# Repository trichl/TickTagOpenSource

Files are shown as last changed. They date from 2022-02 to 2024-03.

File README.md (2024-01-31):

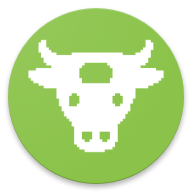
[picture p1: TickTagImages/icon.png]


# I Repository Introduction
This repository contains the entire production-ready design (hardware, software, user interface, 3D-printable housing, assembly instructions) of the open-source TickTag GPS logger.

# II Hardware Production
* See sub folder [TickTagHardware](TickTagHardware)
* Schematics (.sch) and boards (.brd) are designed in Autodesk Eagle 9.5.2
* PCBs were produced and assembled by [PCBWay](https://www.pcbway.com) (production-ready Gerber files and PCBWay settings in [TickTagHardware/GerberProductionFiles](TickTagHardware/GerberProductionFiles))
* Production settings:
   * **REV3**: 24.9 x 10.5 mm, 2 layers, 0.15 mm thickness (flex), 0.35 mm min hole size, immersion gold (ENIG) surface finish (1U"), 0.06 mm min track spacing, 1 oz Cu finished copper, polyimide flex material

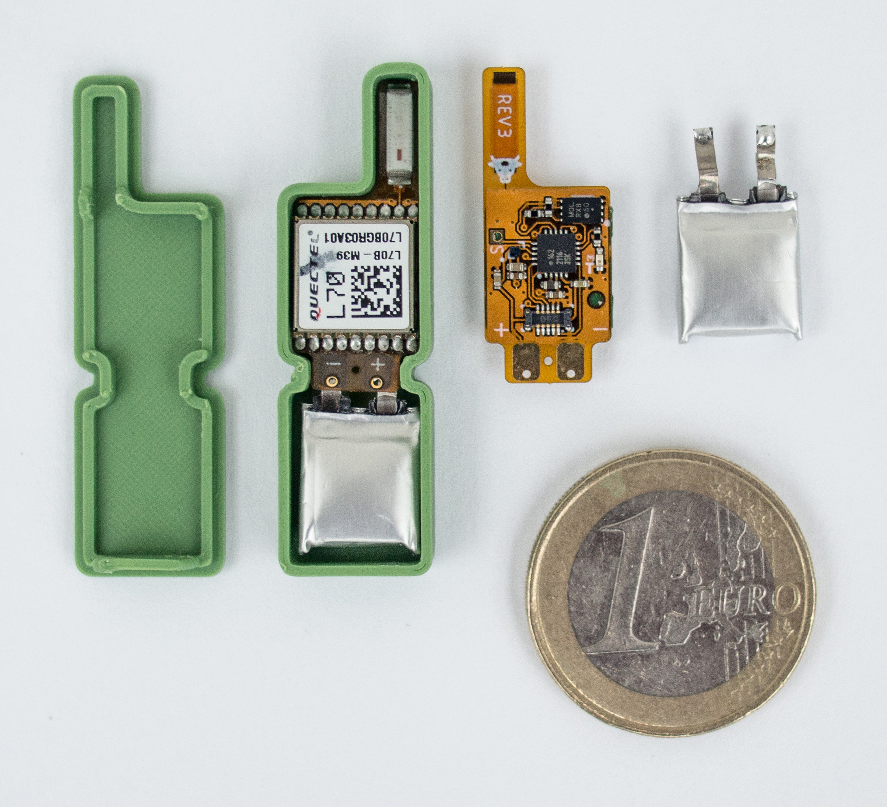
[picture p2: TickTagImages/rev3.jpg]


   * **REV4**: 23.61 x 10.06 mm, 2 layers, 0.2 mm thickness, 0.25 mm min hole size, immersion gold (ENIG) surface finish (1U"), tenting vias, 5/5 mil min track spacing, 1 oz Cu finished copper, FR-4 TG150 material

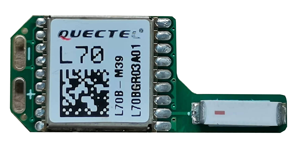
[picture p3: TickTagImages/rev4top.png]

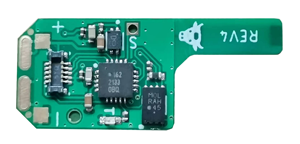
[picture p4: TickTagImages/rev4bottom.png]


   * **User interface board**: 66.4 x 17.8 mm, 2 layers, 1 mm thickness, 0.3 mm min hole size, immersion gold (ENIG) surface finish (1U"), tenting vias, 6/6 mil min track spacing, 1 oz Cu finished copper, FR-4 TG130 material
* Differences between REV3 and REV4:
   * 0.2 mm PCB instead of 0.15 mm (more robust)
   * PCB slots instead of pads for soldering LiPos directly to the PCB
   * New load switch (SiP32431DNP3-T1GE4), as the old load switch has long lead times
   * Reduced the footprint sizes of some of the capacitors and resistors from 0402 to 0201

# III Programming and Assembly

## IDE for Software Development (Windows)
* Atmel Studio 7.0: https://www.microchip.com/en-us/tools-resources/develop/microchip-studio
* Programming language: C / C++

## Android App
* Developed in Android Studio 3.5.1: https://developer.android.com/studio

## Using an Arduino Nano for Flashing
* Follow the instructions on https://github.com/ElTangas/jtag2updi
* The 4.7k resistor is already integrated on the user interface board and does not need to be added
* Alternatively software can be flashed with the official Atmel-ICE: https://www.microchip.com/en-us/development-tool/ATATMEL-ICE

## Flashing the Firmware
Flashing should be done before soldering a battery to the tag.

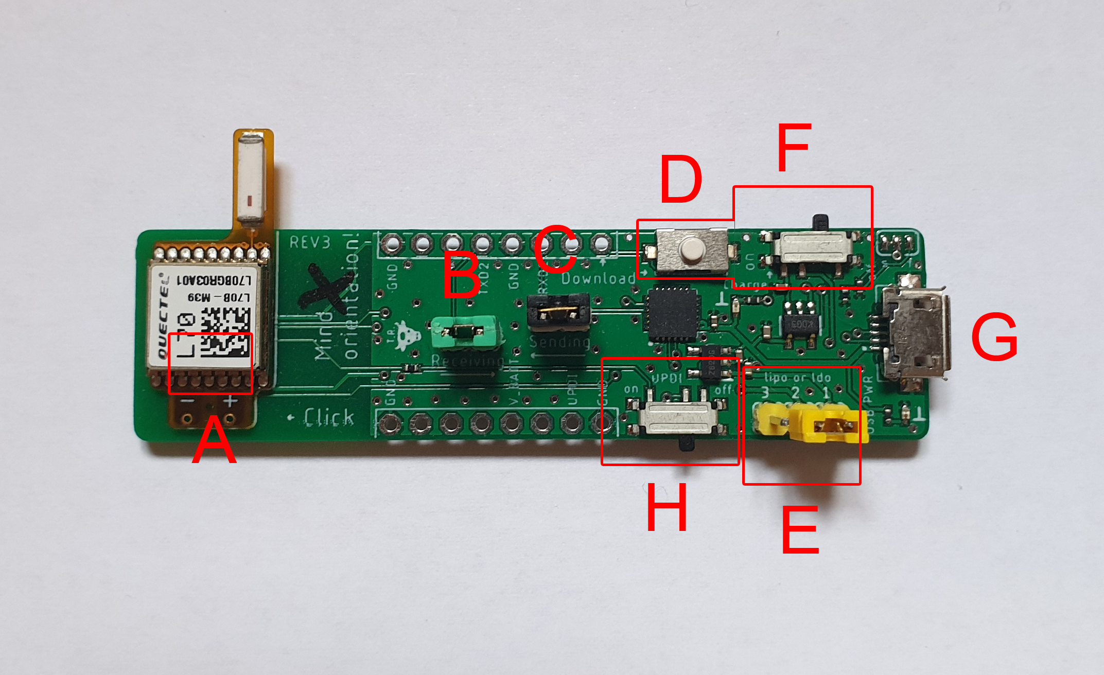
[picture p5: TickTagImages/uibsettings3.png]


1. Check if the yellow jumper (E) connects "1" and "2" ("ldo")
2. Gently click the tag on the user interface board (without battery attached to it) (A), mind the correct orientation of the tag
3. Connect D6 of the Arduino Nano to the UPDI pin of the user interface board (or use an Atmel-ICE instead of an Arduino Nano)
4. Connect the user interface board to a computer (red LED turns on) (G), connect the Arduino Nano to the same computer
5. Slide the UPDI button on the user interface board (H) to ON
6. Go to [TickTagProgramming/avrdude](TickTagProgramming/avrdude), open ScriptWriteFuses_ATTINY1626.bat (or ScriptWriteFuses_ATTINY1616.bat, if you use the 1616) with a text editor and enter the COM port of the Arduino Nano on your computer
7. Execute ScriptWriteFuses_ATTINY1626.bat to write the configuration fuses of the ATTINY.
( It may be possible that executing the script raises an error ie. missing dll file. In this case, try to download and install WinAVR [here](https://sourceforge.net/projects/winavr/) )
8. Open Atmel Studio 7.0 and load the project [TickTagSoftwareBurst](TickTagSoftwareBurst) (you might need to setup the project first, and set the current device to ATtiny1626)
9.  
    1.  Configure the ATTINY programming via Arduino Nano under Tools -> External Tools
    2.  To choose the command, select the three dots and find the location of the TickTagOpenSource repository. Then navigate to TickTagProgramming\avrdude\bin and select avrdude.exe
    3.  For the Arguments: "-P COM7 -c jtag2updi -p t1626 -U flash:w:$(ProjectDir)Debug\\$(TargetName).hex:i", COM7 needs to be replaced with the COM port of the Arduino Nano:

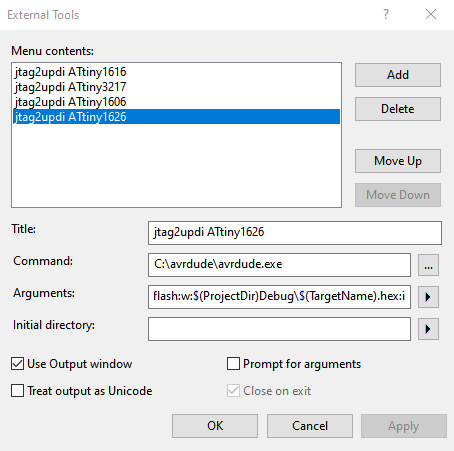
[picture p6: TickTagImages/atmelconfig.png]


10. Press F7 to compile the firmware
11. Press Tools -> jtag2updi ATtiny1626 to flash the firmware

## Tag Assembly

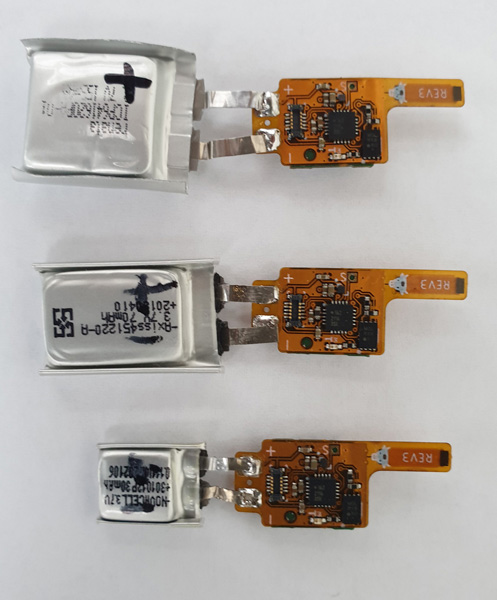
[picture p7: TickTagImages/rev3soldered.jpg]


* If the firmware is successfully flashed onto the microcontroller you can solder a battery to the TickTag battery terminals (plus and minus is written on the tag)
* No battery protection circuit is needed, the battery is protected by software
* You can use a glass fiber pen to roughen the LiPo tabs, which makes soldering of the aluminium tabs more easy (e.g., with a Laeufer 69119 pen)
* Keep the soldering work on the LiPo very short, otherwise the battery might be damaged due to high temperatures
* Keep the area below the TickTag as flat as possible, otherwise you might not be able to click the tag on the user interface board anymore

# IV Tag Manual

## Charging the Battery
**WARNING**: never connect the TickTag to the user interface board when the 3-pin jumper is set to "ldo", otherwise the LiPo will be damaged permanently. The battery can be recharged directly on the breakout board:

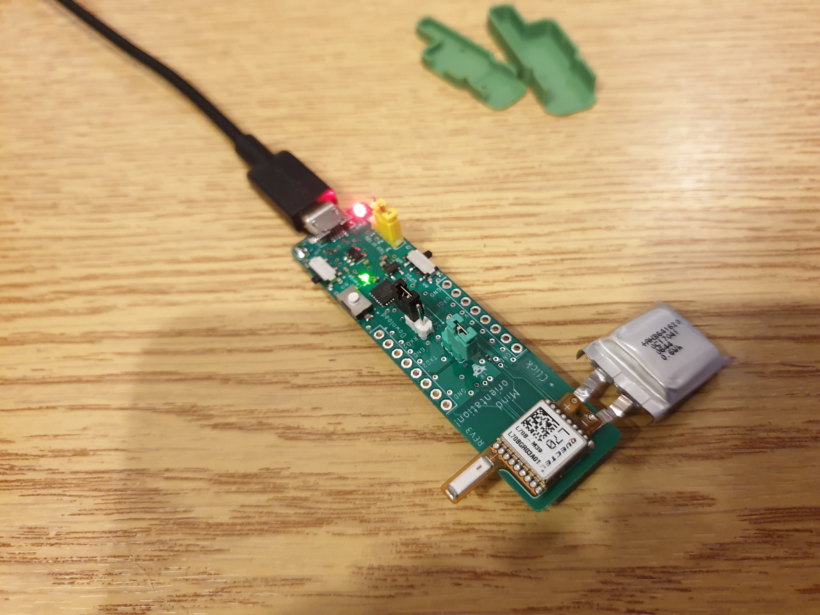
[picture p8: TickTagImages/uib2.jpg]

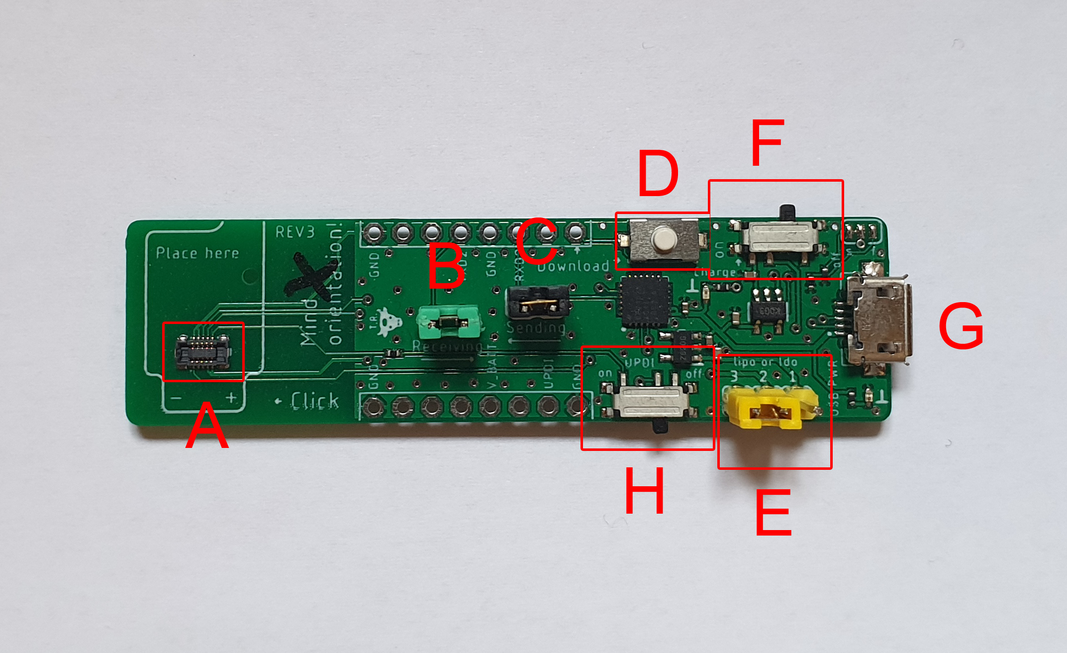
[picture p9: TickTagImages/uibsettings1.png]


1. Check if the yellow jumper connects (E) "3" and "2" ("lipo")
2. Gently click the tag on the user interface board (with battery attached to it) (A), mind the correct orientation of the tag
3. Connect the USB connector to a computer or powerbank (red LED turns on) (G)
4. Slide the charge button on the user interface board (F) to the left (ON)
5. A green LED on the user interface board turns on and indicates that the battery is being charged
6. In case the tag was previously activated, it first needs to be deactivated:
   * Wait some minutes until battery is charged a bit
   * Press the white button (D) for 5 seconds to restart the tag and enter menue
   * Green LED on the tag will blink 5 times to indicate download mode and system restart
7. Wait until the green LED on the user interface board turns off (battery charged)
   * This can take hours (default charge current: 15 mA)
   * For example: an empty 30 mAh lipo battery needs 2 hours to be fully charged
   * For example an empty 120 mAh lipo battery needs 8 hours to be fully charged
8. The tag can be activated again (see chapter "Activation")
   * Warning: If the memory is full the tag can not be reactivated (data download necessary, see chapter "Data Download, Configuration and Memory Reset")

## Activation
* Prerequisites
   * The tags need to be connected to a charged lithium polymer battery (plus and minus pads on the tag are soldered to the battery)
   * If the battery voltage is too low, the tag won’t start (please charge the battery), see chapter "Charge Battery"
   * If the data memory is full, the tag won't start (please download the data and reset the memory), see chapter "Data Download, Configuration and Memory Reset"
   * Check the location of the green LED on the tag (it will give you visual feedback):

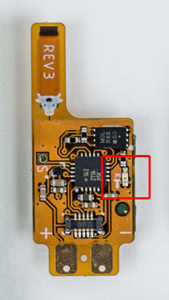
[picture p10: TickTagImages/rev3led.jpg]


### Activation option 1: by a wire

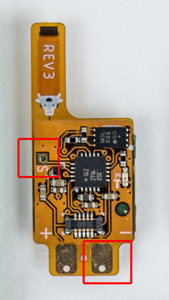
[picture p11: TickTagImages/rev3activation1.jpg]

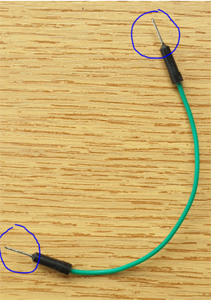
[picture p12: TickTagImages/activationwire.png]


1. Gently touch with one end of a conducting wire the ground connection where the battery minus is soldered to
2. Gently touch with the other end of the wire the hole marked with "A" (or "ST")
3. Once the tag starts blinking green, remove the wire immediately (should not take longer than 2 seconds)
4. The tag blinks 7 times to indicate that it’s activated, then waits for 700 ms and is blinking again to indicate battery status (1 time = battery low, 7 times = battery is full)
5. The green LED is located on the back side of the tag, so it's best to hold the breakout board sideways to see the blinking LED under the tag
6. If it doesn't blink at all: battery voltage might be low or the tag is already activated
7. If the tag blinks 5 times it entered download mode (was already activated), please wait a minute and start again from the beginning
8. The tag is activated and will start sampling GPS data after 10 seconds (default configuration, can be changed, see chapter "Data Download, Configuration and Memory Reset")

### Activation option 2: on breakout board

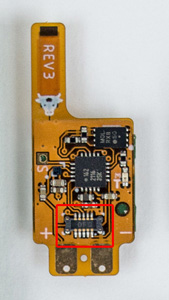
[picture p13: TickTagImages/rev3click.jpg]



1. Locate the click connector on the tag (see picture above)
2. Take a look at the breakout board, do not connect the USB power connector (G) to the computer or phone (no external power needed for activation)
3. Gently click the tag on the user interface board (with battery attached to it) (A), mind the correct orientation of the tag
      * Take care of the correct orientation of the tag as shown in the photo, otherwise a short circuit might permanently damage the tag
4. Now press the white button (D) for two seconds until the tag starts to blink
      * Do not press the button longer than some seconds
      * The tag blinks 7 times to indicate that it’s activated, then waits for 700 ms and is blinking again to indicate battery status (1 time = battery low, 7 times = battery is full)
      * The green LED is located on the back side of the tag, so it's best to hold the breakout board sideways to see the blinking LED under the tag
      * If it doesn't blink at all: battery voltage might be low or the tag is already activated
      * If the tag blinks 5 times it entered download mode (was already activated), please wait a minute and start again from the beginning
5. The tag is activated and will start sampling GPS data after 10 seconds (default configuration, can be changed, see chapter "Data Download, Configuration and Memory Reset")

## After the Activation (Data Sampling)
* After the activation delay, the tag starts blinking green every second and tries to get the current time via GPS satellites. If it can’t obtain the time within 120 seconds, it will sleep for 15 minutes and will try again.
   * **IMPORTANT**: If blinking configuration is set to false the tag will completely stop blinking at all after getting the current UTC time
   * If you have configured the tag to only sample GPS at certain times:
       * **IMPORTANT**: Before attaching the tag to the animal (e.g., the day before): go outside, activate the tag, wait until it starts blinking, wait until the green LED stays on for 2 seconds (tag got the time and went to sleep mode).
* The tag samples GPS data (continuously or from time to time, depending on the configuration)
* The module deactivates itself if the battery voltage is low (default configuration: 3.3V) or if the memory is full (maximum 13,100 fixes)

## On-Animal Mounting
* **IMPORTANT**: The small antenna of the TickTag is disturbed by any electrically conducting material nearby, so keep the antenna away from other tags, VHF/UHF tags, batteries, screws or similar materials (at least 5 cm).
* **IMPORTANT**: The antenna can easily break if bent too strong. Try to protect the antenna with a 3D-printed housing (for example with ASA material).
* **IMPORTANT**: The battery needs to be located behind the tag (see picture below), never under the tag, as it will disturb the antenna.
* **IMPORTANT**: Mount the tag on the flat side (connector facing down, top side with antenna facing the sky). The photo shows the top side that should face the sky:

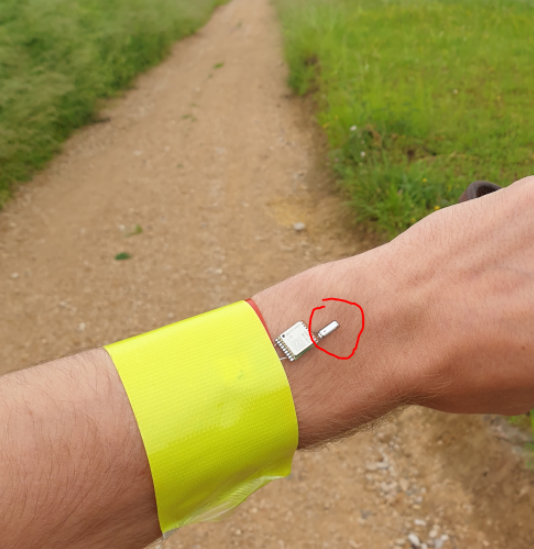
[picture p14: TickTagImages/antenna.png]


* **IMPORTANT**: Do not glue anything on the connector that can't be removed, otherwise data cannot be downloaded (Bostik Blu Tack is a glue that can be easily removed afterwards):



## Data Download, Configuration and Memory Reset


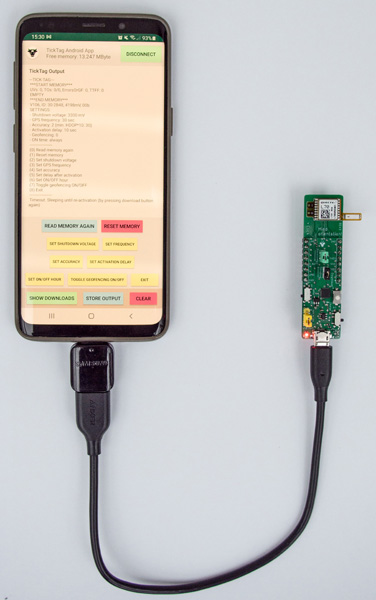
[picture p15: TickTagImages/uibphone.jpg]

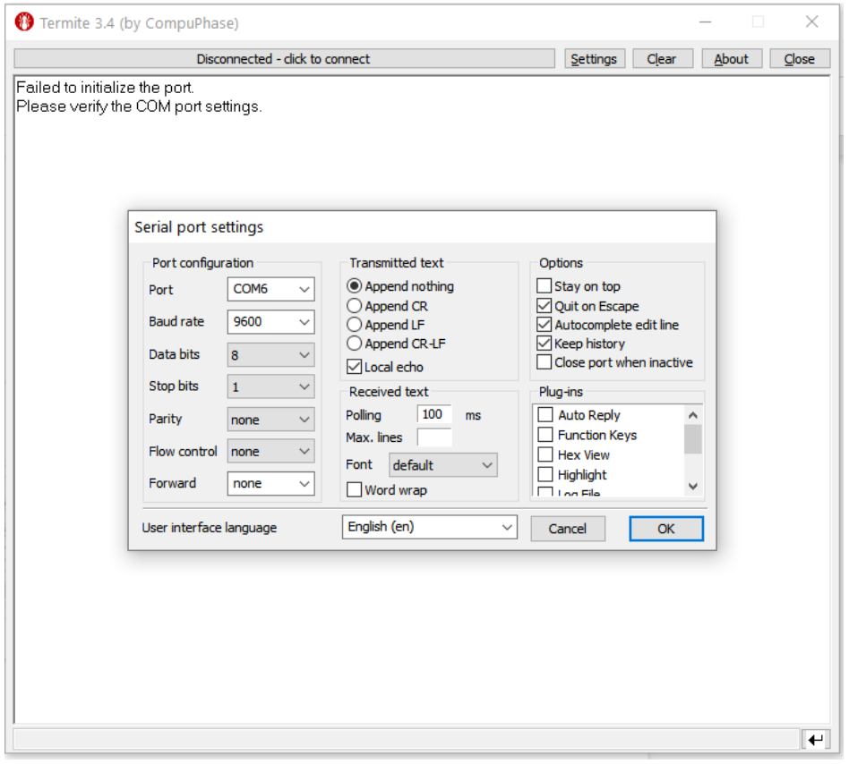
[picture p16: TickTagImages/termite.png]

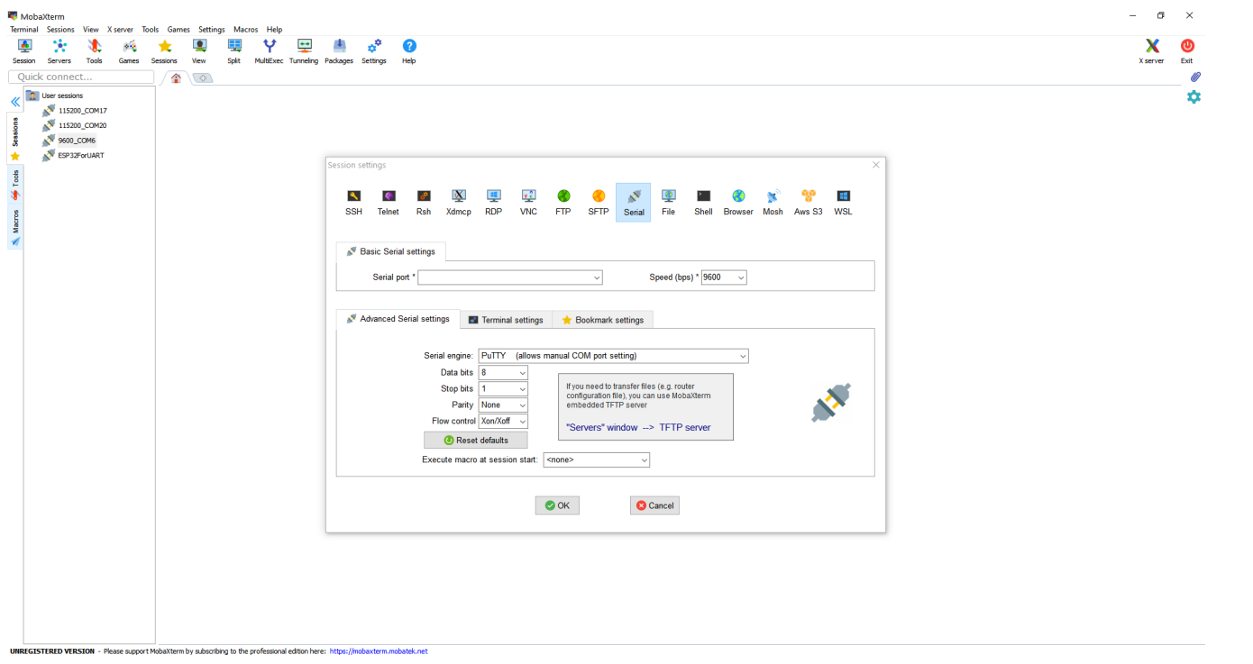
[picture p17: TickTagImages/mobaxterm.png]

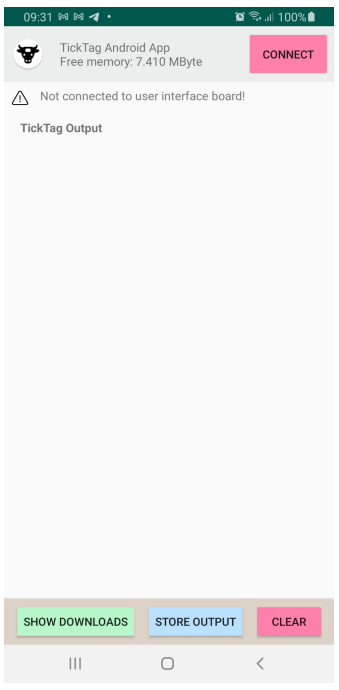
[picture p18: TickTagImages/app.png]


1. Choose a serial software
   * **Option 1**: Download a serial program for your computer
       * For example (Windows 10): Termite: https://www.compuphase.com/software_termite.htm (see screenshot above for configuration)
       * For example (Windows 10): MobaXTerm: https://mobaxterm.mobatek.net/ (see screenshot above for configuration)
       * The Arduino Serial Monitor also works fine
   * **Option 2**: Use the TickTag Android app [TickTagAndroidApp](TickTagAndroidApp) and an USB OTG adapter to connect the breakout board with the phone
2. The battery needs to be connected (soldered) to the tag
3. Check if the yellow jumper connects (E) "3" and "2" ("lipo")
4. Gently click the tag on the user interface board (with battery attached to it) (A), mind the correct orientation of the tag
5. Connect the USB connector to a computer or Android phone (red LED turns on) (G)
6. Slide the charge button on the user interface board (F) to the left (ON) to charge the battery while downloading data (not mandatory, but recommended)
7. **For option 1**: Open the serial program on your computer with following settings:
   * COM port: select the CP2104N COM port from the list
   * Baud rate: 9600
   * Default serial settings (8 data bits, 1 stop bit, no parity)
8. Click on CONNECT in your serial program or the Android app
9. Press the download button (D) for 5 seconds (not longer) until the green LED on the tag blinks for 5 times
10. Data download is shown in your serial program (in CSV format)
11. After the download the tag shows a little menu for configuration
       * Data download might take some minutes (if memory is full)
       * Data download can be interrupted by pressing the download button once (short), data will not be deleted
12. In the command line of your serial program enter "1" and press return to reset the memory (when using the Android app: press the "Reset memory" button)
13. The tag will confirm that the memory is now empty
14. The tag will restart into the activation state after some time (waiting on tag activation, see chapter "Activation")

Example data output of the serial program (or Android app):

```
---TICK-TAG---
*START MEMORY*
UVs: 0, TOs: 0/0, ErrorsOrGF: 0, TTFF: 68
Fixes: 10, Avg. TTF: 11 s, Avg. HDOP (x10): 16
count,timestamp,lat,lon
1,1635235981,47.74340,8.99910
2,1635236130,47.74346,8.99922
3,1635236352,47.74340,8.99889
4,1635236506,47.74327,8.99894
5,1635236682,47.74336,8.99879
6,1635238092,47.74340,8.99824
7,1635238313,47.74304,8.99896
8,1635238411,47.74329,8.99883
9,1635238511,47.74332,8.99878
10,1635238610,47.74325,8.99881
*END MEMORY*
V201, ID: 30-2509, 3533mV, 01b
SETTINGS:
- Min voltage: 3300 mV
- Frequency: 90 s
- Min HDOP (x10): 30
- Activation delay: 60 s
- Geofencing: 0
- Burst duration: 0 s
- Time: 8:00 - 14:00 UTC

0 Read memory
1 Reset memory
2 Set min. voltage
3 Set frequency
4 Set accuracy
5 Set activation delay
6 Set times
7 Toggle geofencing ON/OFF
8 Set burst duration
9 Exit
```

## Configuration Parameters
* **Read memory**: printing all stored GPS fixes as CSV-compatible list (count, timestamp in UTC, latitude, longitude)
* **Reset memory**: deleting all stored GPS fixes
* **Min. voltage (3000 - 4250, in mV)**: recording is stopped when battery voltage (open-circuit, no load) drops below that threshold
* **Frequency (1 - 16382, in s)**: GPS fix attempt frequency, between 1 and 5 s the TickTag keeps the GPS module constantly powered and puts the device in fitness low power mode
* **Accuracy (1 - 250, HDOP x 10)**: HDOP value (times 10, 30 = 3.0) that tries to be achieved within 9 seconds after getting the first positional estimate
* **Activation delay (10 - 16382, in s)**: delay after activation before the tag starts recording data
* **Sampling times (0000 - 2359, time within day)**: daily recording time window
* **Geo-fencing (true/false)**: if set to true the first GPS fix becomes the home location and only fixes outside a 300 m radius are stored (10 min hibernation afterwards)
* **Blinking (true/false)**: if set to true the tag blinks every second when GPS is active

## Default Configuration
* After flashing the firmware the default configuration is set to:
* **Min. voltage (3000 - 4250, in mV)**: 3000
* **Frequency (1 - 16382, in s)**: 30
* **Accuracy (1 - 250, HDOP x 10)**: 30
* **Activation delay (10 - 16382, in s)**: 10
* **Sampling times (0000 - 2359, time within day)**: always on
* **Geo-fencing (true/false)**: false
* **Blinking (true/false)**: false

## State Machine
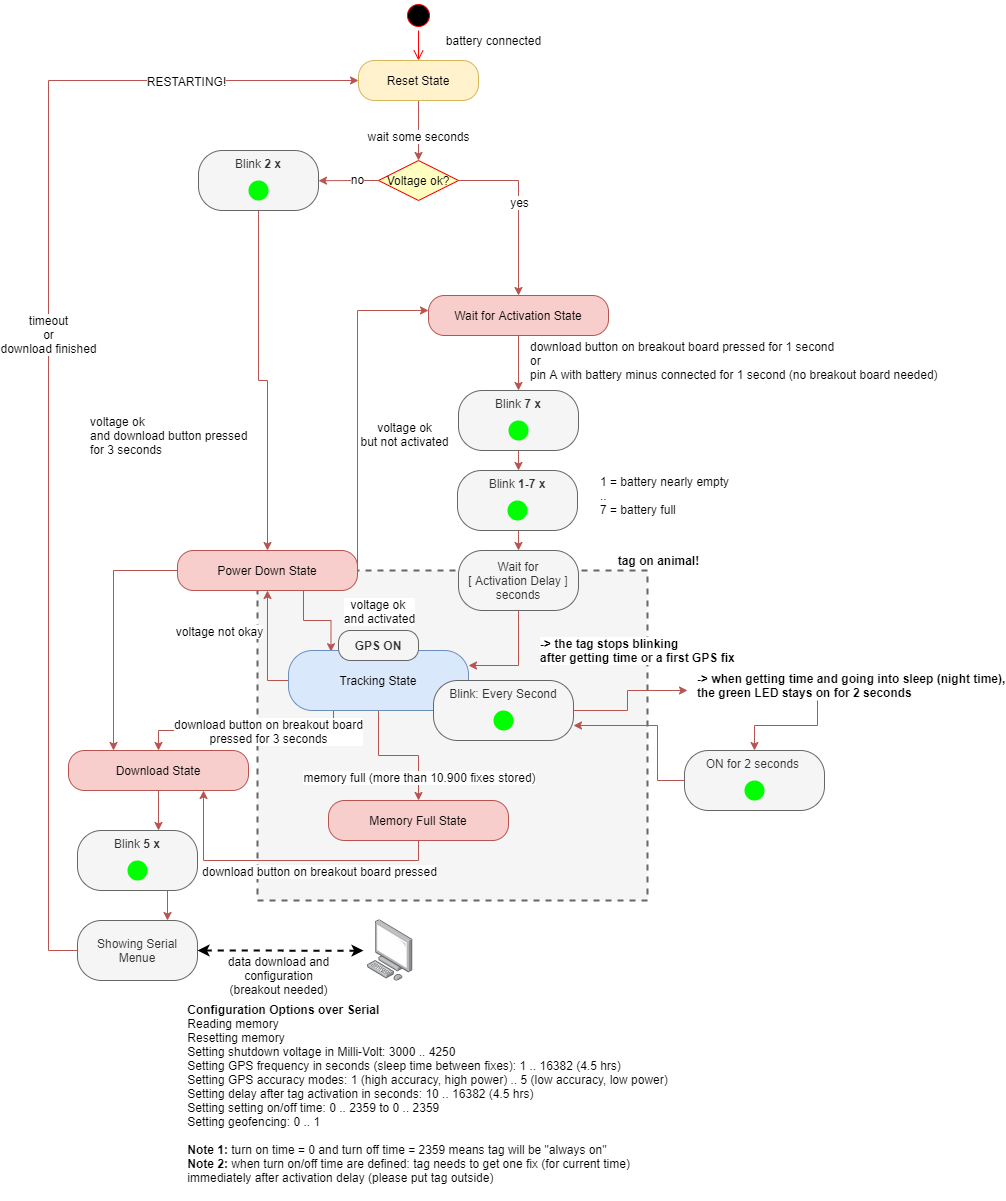
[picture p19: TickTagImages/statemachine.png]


# V Data Compression Algorithm
GPS data is stored on the 128 kByte EEPROM with a lossless compression algorithm. GPS positions are stored with 5 decimal places (accuracy: 1.11 m).

* **Latitute (A)**: stored in 25 Bit (unsigned): compressedLatitude = (latitude * 100000) + 9000000
* **Longitude (B)**: stored in 26 Bit (unsigned): compressedLongitude = (longitude * 100000) + 18000000
* **Timestamp (C)**: stored in 29 Bit  (unsigned): compressedTimestamp = timestamp - 1618428394
* Storage pattern of Bits: **AAAAAAAA AAAAAAAA AAAAAAAA ABBBBBBB BBBBBBBB BBBBBBBB BBBCCCCC CCCCCCCC CCCCCCCC CCCCCCCC**
* Total length: 10 Byte per GPS fix

# VI 3D-printed Housings
* Check [TickTag3DPrints](TickTag3DPrints) for .STL files (designed in Fusion 360)
* Housings were printed with ASA filament on a Prusa Mini (0.4 mm nozzle)
* PrusaSlider 2.2.0 settings: 0.45 mm extrusion width, 0.10 mm DETAIL settings

# VII Data
* Check [TickTagData](TickTagData) for data results

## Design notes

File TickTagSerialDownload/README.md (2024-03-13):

# TickTag Serial Download Tool Documentation

This tool allows the user to *get the serial data from a TickTag device*, then *arrange the data in csv files*.
One folder is created for each day at which tags have been activated, in these folders two files are created per tag :
1. The **log files** which includes **all the serial output** from the tag
2. The **csv files** containing **GPS data** that have been automatically extracted from the serial data

The tool also supports memory resetting : You can choose at the end of the download process between keeping data on the tag on resetting the tag memory.

## Prerequisites

1. Using this assume you are using TickTag REV6 and the breakout board.
2. You have a Python version > 3.6 ( You can download it from [https://www.python.org/downloads/] )
3. You have all the python dependencies libraries installed : 
   To make sure, go to the SerialDownload base folder and run ```pip install requirements.txt```

## Usage

1. Make sure all the jumpers are on the breakout board : Receiving, Sending and if a battery is attached, make sure the jumper is set to lipo, otherwise set it to ldo. Both *UPDI* and *charge* switches should be *OFF*.
2. Plug the board to an USB port on your computer and find the serial port associated.
3. Open the python script *TickTag_Serial_Doynload.py* with any text editor and change line 11 : ```PORT="COM12"``` ( modify COM12 to the Serial USB port used by the breakout board on your computer ).
4. Gently click the tag on the breakout board
5. Click the button on the breakout board for 2s ( no more than 3s ) and wait : 
   1. If the green LED blinks 7 times and then 1 to 7 times, it means the tag is now active
   2. If nothing blinks, it means the tag was probably already active, leave it this way
6. Launch the python script -> run ```python TickTag_Serial_Download.py``` in the terminal.
7. You can than click the button on the breakout board for 6s until the green LED starts blinking.
8. A progress bar should prompt you with the data downloading status, and the script should ask you if you want to reset the memory => At this point all the data should already be saved in files but make sure to check.
9.  Data downloading is done.

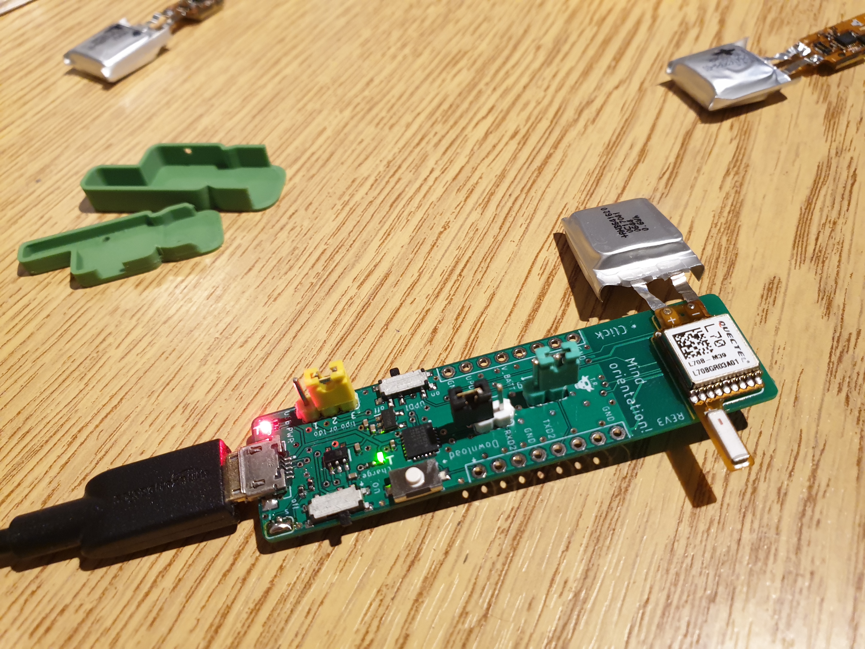
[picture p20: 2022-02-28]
TickTagImages/uib3.jpg

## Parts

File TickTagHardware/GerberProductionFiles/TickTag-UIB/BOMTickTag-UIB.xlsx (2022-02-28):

Item | Designator | Value | Manufacturer | Manufacturer Part Number | Package/Footprint | Type
1 | U1 | CP2102N | Silicon Labs | CP2102N-A02-GQFN24 | QFN-24 | SMD
2 | U2 | MCP73831 | Microchip | MCP73831T-2ACI/OT | SOT-23 | SMD
3 | U3 | AXE510127 | Panasonic Industrial Devices | AXE510127 | - | SMD
4 | LDO42 | R1172N421D-TR-FE | Ricoh Electronic Devices Company | R1172N421D-TR-FE | SOT-23-5 | SMD
5 | CHRG_SWITCH | PCM12SMTR | C&K | PCM12SMTR | - | SMD
6 | UPDI_SWITCH | PCM12SMTR | C&K | PCM12SMTR | - | SMD
7 | RESET_SWITCH | 434111025826 | Wurth Elektronik | 434111025826 | - | SMD
8 | USB_CON | 629105136821 | Wurth Elektronik | 629105136821 | - | SMD
9 | D1 | RED | Kingbright | APHHS1005LSECK/J3-PF | 0402 (1005 metric) | SMD
10 | D2 | GREEN | Kingbright | APHHS1005CGCK | 0402 (1005 metric) | SMD
11 | C_USB | 0.1uF | Murata | GCM155R71C104KA55D | 0402 (1005 metric) | SMD
12 | C_CHRG1 | 4.7uF | AVX | 0402YD475MAT2A | 0402 (1005 metric) | SMD
13 | C_CHRG2 | 4.7uF | AVX | 0402YD475MAT2A | 0402 (1005 metric) | SMD
14 | C_LDO1 | 4.7uF | AVX | 0402YD475MAT2A | 0402 (1005 metric) | SMD
15 | C_LDO2 | 4.7uF | AVX | 0402YD475MAT2A | 0402 (1005 metric) | SMD
16 | R_CHRG1 | 2k | - | Generic 0402 (1005 metric) Resistor (+/- 1%) | 0402 (1005 metric) | SMD
17 | R_LED | 2k | - | Generic 0402 (1005 metric) Resistor (+/- 1%) | 0402 (1005 metric) | SMD
18 | R_UPDI | 4.7k | - | Generic 0402 (1005 metric) Resistor (+/- 1%) | 0402 (1005 metric) | SMD
19 | R_CHRG2 | 20k | - | Generic 0402 (1005 metric) Resistor (+/- 1%) | 0402 (1005 metric) | SMD
20 | R_CHRG3 | 67k | - | Generic 0402 (1005 metric) Resistor (+/- 1%) | 0402 (1005 metric) | SMD

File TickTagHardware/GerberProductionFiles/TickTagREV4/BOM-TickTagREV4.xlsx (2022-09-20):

Item | Designator | Value | Manufacturer | Manufacturer Part Number | Package/Footprint | Type
1 | ANT-CHIP | ANT1 | Johanson Technology Inc. | 1575AT43A0040E | - | SMD
2 | ATTINY | ATTINY1626-MFR | Atmel | ATTINY1626-MFR | QFN-20 | SMD | ATTINY1616-MFR also possible
3 | AXE | AXE610124 | Panasonic | AXE610124 | - | SMD
4 | L70 | L70 | Quectel | L70B-M39 | - | SMD
5 | LS | SIP32431DNP3-T1GE4 | Vishay Semiconductors | SIP32431DNP3-T1GE4 | TDFN4 | SMD
6 | MEM | CAT24M01HU5I-GT3 | ON Semiconductor | CAT24M01HU5I-GT3 | UDFN-8 | SMD
7 | C_BCK1 | 0.1 uF | Murata | GRM033C71C104KE14J | 0201 (0603 metric) | SMD
8 | C_L701 | 0.1 uF | Murata | GRM033C71C104KE14J | 0201 (0603 metric) | SMD
9 | C_LS2 | 0.1 uF | Murata | GRM033C71C104KE14J | 0201 (0603 metric) | SMD
10 | C_LS | 1uF | Murata | GRM155R70J105KA12D | 0402 (1005 metric) | SMD
11 | C_TINY | 1uF | Murata | GRM155R70J105KA12D | 0402 (1005 metric) | SMD
12 | C_BCK2 | 4.7uF | TDK | C1005X5R1A475K050BC | 0402 (1005 metric) | SMD
13 | C_L702 | 10uF | Murata | ZRB15XR61A106ME01D | 0402 (1005 metric) | SMD
14 | D_LED_GREEN | GREEN | Kingbright | APHHS1005CGCK | 0402 (1005 metric) | SMD
15 | R_LED | 1k | - | Generic 0201 (0603 metric) Resistor (+/- 1%) | 0201 (0603 metric) | SMD
16 | R_SCL | 4.7k | - | Generic 0201 (0603 metric) Resistor (+/- 1%) | 0201 (0603 metric) | SMD
17 | R_SDA | 4.7k | - | Generic 0402 (1005 metric) Resistor (+/- 1%) | 0402 (1005 metric) | SMD

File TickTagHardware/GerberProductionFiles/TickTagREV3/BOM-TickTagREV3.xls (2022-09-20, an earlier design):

Item | Designator | Value | Manufacturer | Manufacturer Part Number | Package/Footprint | Type
1 | ANT-CHIP | ANT1 | Johanson Technology Inc. | 1575AT43A0040E | - | SMD
2 | ATTINY | ATTINY1626 | Atmel | ATTINY1626-MFR | QFN-20 | SMD | ATTINY1616-MFR also possible
3 | C_BCK1 | 0.1uF | Murata | GCM155R71C104KA55D | 0402 (1005 metric) | SMD
4 | C_L701 | 0.1uF | Murata | GCM155R71C104KA55D | 0402 (1005 metric) | SMD
5 | C_TINY | 1uF | Murata | GRM155R70J105KA12D | 0402 (1005 metric) | SMD
6 | C_TPS | 1uF | Murata | GRM155R70J105KA12D | 0402 (1005 metric) | SMD
7 | C_BCK2 | 4.7uF | TDK | C1005X5R1A475K050BC | 0402 (1005 metric) | SMD
8 | C_L702 | 10uF | Murata | ZRB15XR61A106ME01D | 0402 (1005 metric) | SMD
9 | D_LED_GREEN | GREEN | Kingbright | APHHS1005CGCK | 0402 (1005 metric) | SMD
10 | L70 | L70 | Quectel | L70B-M39 | - | SMD
11 | MEM | CAT24M01HU5I-GT3 | ON Semiconductor | CAT24M01HU5I-GT3 | UDFN-8 | SMD
12 | R_LED | 1k | - | Generic 0402 (1005 metric) Resistor (+/- 1%) | 0402 (1005 metric) | SMD
13 | R_SCL | 4.7k | - | Generic 0402 (1005 metric) Resistor (+/- 1%) | 0402 (1005 metric) | SMD
14 | R_SDA | 4.7k | - | Generic 0402 (1005 metric) Resistor (+/- 1%) | 0402 (1005 metric) | SMD
15 | U1 | AXE610124 | Panasonic | AXE610124 | - | SMD
16 | U6 | TPS22916 | Texas Instruments | TPS22916CN | DSBGA-4 | SMD

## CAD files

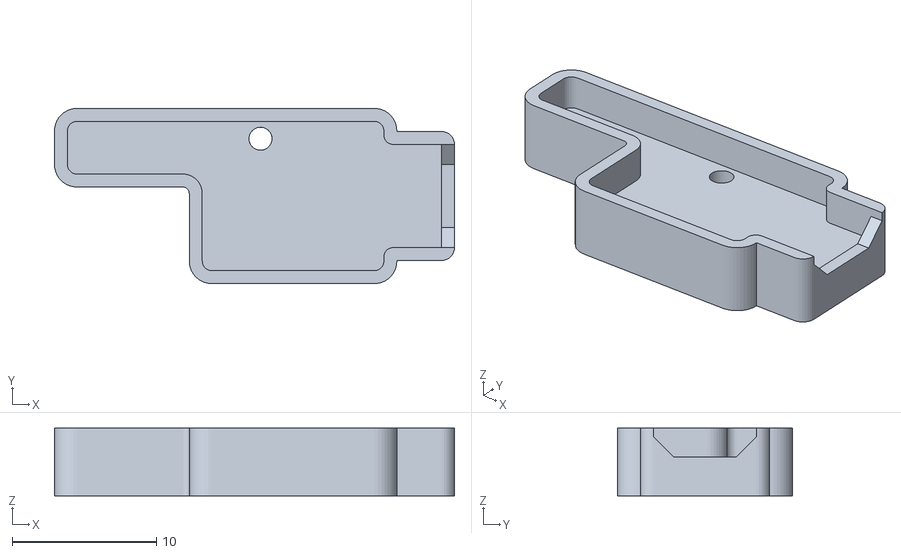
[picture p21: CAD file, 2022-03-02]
TickTag3DPrints/REV3/TTHousingLiPoOutside_Bottom.stl
27.8 x 12.2 x 4.70

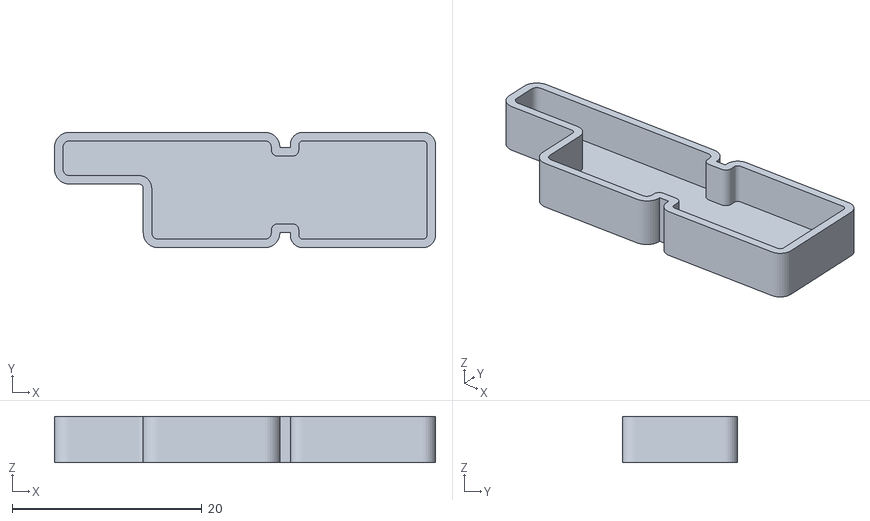
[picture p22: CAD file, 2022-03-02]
TickTag3DPrints/REV3/TTHousing30mAhV2_Bottom.stl
40.1 x 12.2 x 4.90

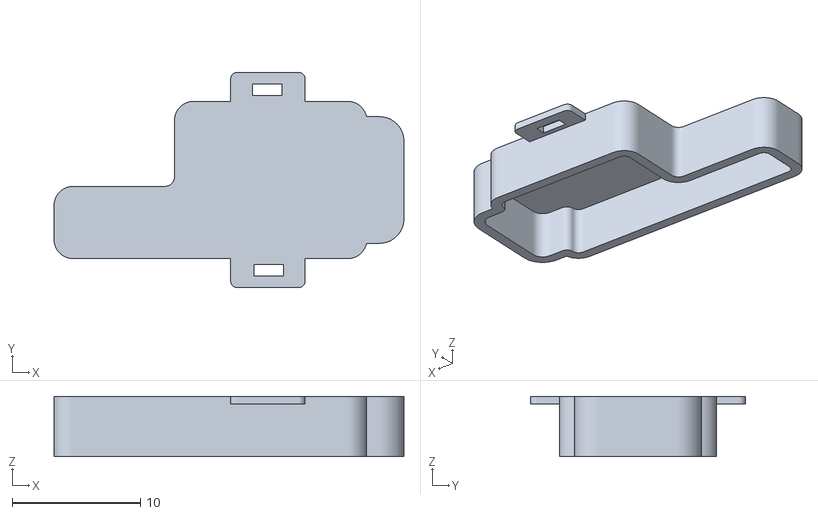
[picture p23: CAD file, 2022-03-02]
TickTag3DPrints/REV3/TTHousing30mAh_Bottom.stl
27.3 x 16.8 x 4.70

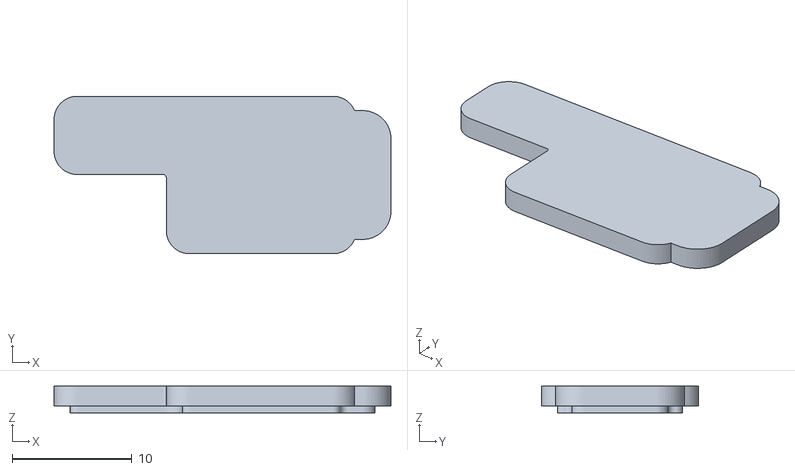
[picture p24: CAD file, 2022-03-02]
TickTag3DPrints/REV3/TTHousing30mAh_Lid.stl
28.2 x 13.2 x 2.25

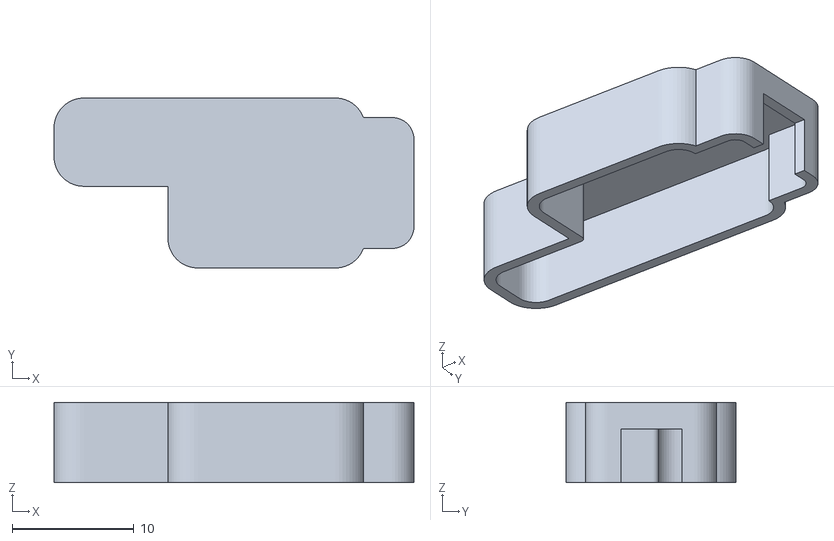
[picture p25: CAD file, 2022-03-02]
TickTag3DPrints/REV3/TTHousingLiPoOutside_Lid.stl
29.5 x 13.9 x 6.60

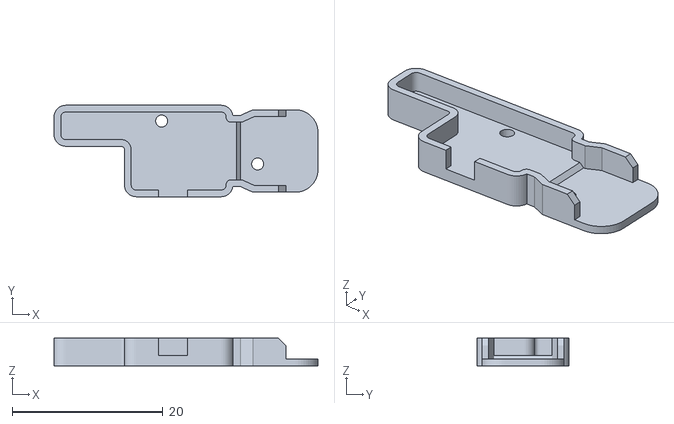
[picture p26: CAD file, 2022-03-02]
TickTag3DPrints/REV3/TTHousing165mAh_Bottom.stl
35.1 x 12.2 x 3.70

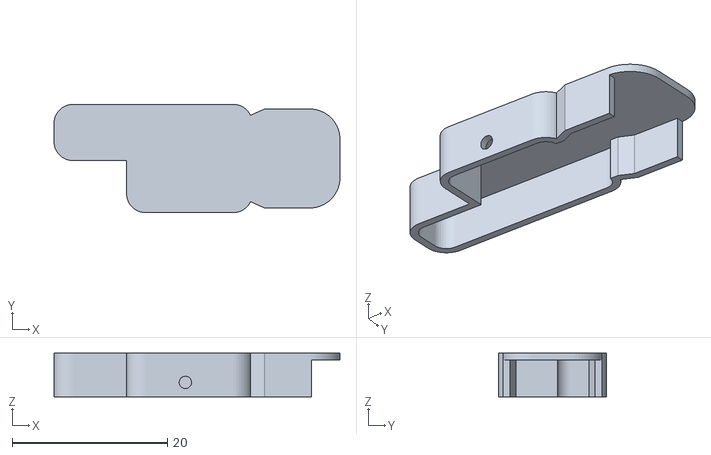
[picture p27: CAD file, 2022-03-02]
TickTag3DPrints/REV3/TTHousing165mAh_Lid.stl
36.8 x 13.9 x 5.67

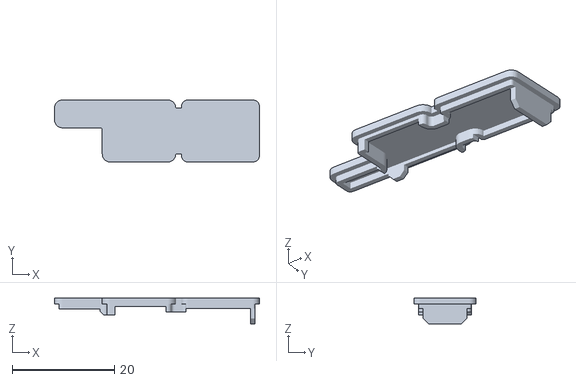
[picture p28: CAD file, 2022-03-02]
TickTag3DPrints/REV3/TTHousing30mAhV2_Lid.stl
40.1 x 12.2 x 5.00

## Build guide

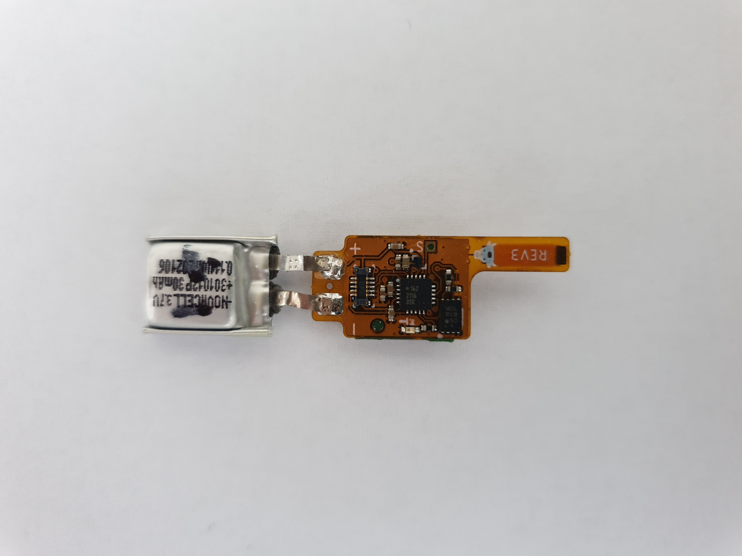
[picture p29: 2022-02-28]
TickTagImages/rev3soldered2.jpg

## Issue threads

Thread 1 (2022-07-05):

trichl/TickTagOpenSource #1: Battery runtime

padok, 2022-07-05:
Hi there,

I am very interested in your project, but my use case is a little different. 
I would like to track my animals for a year and wonder what is the average power consumption of the tick tag is if, for example, 3 GPS positions are recorded every day. Very low power setup, as far as I can tell the EEPROM size allows ~35 recordings per day within a year (I would also be interested in data with this setting).
I would like to calculate how many, say, 1500 mAh AA alkaline batteries are needed to run the device for a year.
Do you have any data that could help me figure this out and are you willing to provide it to me?

Thanks in advance!

padok, 2022-07-06:
Thanks for your quick reply!

I mainly want to avoid lipos because I can't make sure that the lipos will operate in their optimal temperature range and their low shelf life is a concern to me. My plan is to connect three AA battery pairs in series, which would give me a voltage range of 2.7V to 4.5V with 6 cells and a capacity of about 15000mAh, which is pretty much what LIPOs deliver at 3.2V to 4.2V. 
Would that work? At what voltage does your firmware shut off? And is 4.5V still in a acceptable range?

From your rough estimation and roughly 3/4 of the battery capacity (4.5V-3.2V) that would mean 30 fixes a day in bad conditions right?

My idea is to maybe replace some TELLUS T3H collars with this setup.

trichl, 2022-07-08:
> Thanks for your quick reply!
>
> I mainly want to avoid lipos because I can't make sure that the lipos will operate in their optimal temperature range and their low shelf life is a concern to me. My [...]

Hi padok, this design is optimized to be ultra light. Such a huge setup is not within the scope of the project and I would recommend using a standard GPS logger off the shelf with a bigger antenna. Any voltage above 4.3V will destroy the logger. The antenna will most probably be detuned by the presence of such a big battery pack. Best

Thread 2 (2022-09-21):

trichl/TickTagOpenSource #2: Discussion of technical tradeoffs?

JimJJewett, 2022-09-21:
Is there a detailed discussion of design tradeoffs somewhere?  (I've read the journal article at https://journals.plos.org/plosone/article?id=10.1371/journal.pone.0267730 and the project README.)

I was impressed that it made sense to choose a heavier GPS receiver in order to use a smaller battery, so you may well have considered the following as well, but ... I couldn't find the information.

Why use external flash memory instead of the LOCUS logging built in to the GPS chip used by the GPS module?  

Why use a custom logging format?  I assume it was to reduce memory memory usage, but then why not document how to customize it further, by dropping the last few bits (within the HDOP) or the first few (for animals not likely to leave the local area).  Or by storing only differences from the previous fix, which should take fewer bits, at the cost of some software complexity.

Was the ATTiny needed, or would it have been reasonable to use just the GPS module?  As best I could tell, this gave you more freedom for scheduled GPS fixes, but the combination of various low-power modes and conditional capture (including only when outside a home area, or moving faster than a certain speed) seemed like they might outweigh this in some cases.

What about just using the GPS chip (MTK 3337?) instead of a module (Quectel L70?)  This might make it easier to get the right customizations on which data to save and when, but if it also required 5000 units or lots of hardware integration, that could explain why not...

trichl, 2022-09-27:
Hey Jim,

good questions and a good idea :-) With new GPS chips it would for sure be possible to reduce the weight, but key point is the continuous power consumption. New interesting chips are for example the ublox MAX-M10M (max. 3.6V on backup line, means no possibility to use a lipo without LDO) or the YIC71009EBGG (no backup mode though).

I thought about using LOCUS, but it lacks flexibility (sampling schedules, burst recordings, ...) and can only store a maximum of ~3800 fixes. Custom logging format was implemented to reduce memory footprint of a fix without loosing accuracy. HDOP and other performance metrics are not stored alongside a fix, but as a summary only (average value of all fixes). Storing only differences might be an option to further compress the data! The software already integrates geo-fencing, in cases when animals are stationary and only excursions outside their home ranges are of interest.

In the first design approach I tried to use only the L70 without MCU, but it becomes extremely unhandy in the field (you need to send UART configuration messages before starting to record). I think a MCU gives way more flexibility.

Integrating a MTK 3337 or similar GPS chips would also be very interesting, but requires a lot of external components and is not easy (RF-wise).

Happy to keep on discussing.

Best, Timm

trichl, 2022-09-27:
Sorry, accidentially closed the issue.

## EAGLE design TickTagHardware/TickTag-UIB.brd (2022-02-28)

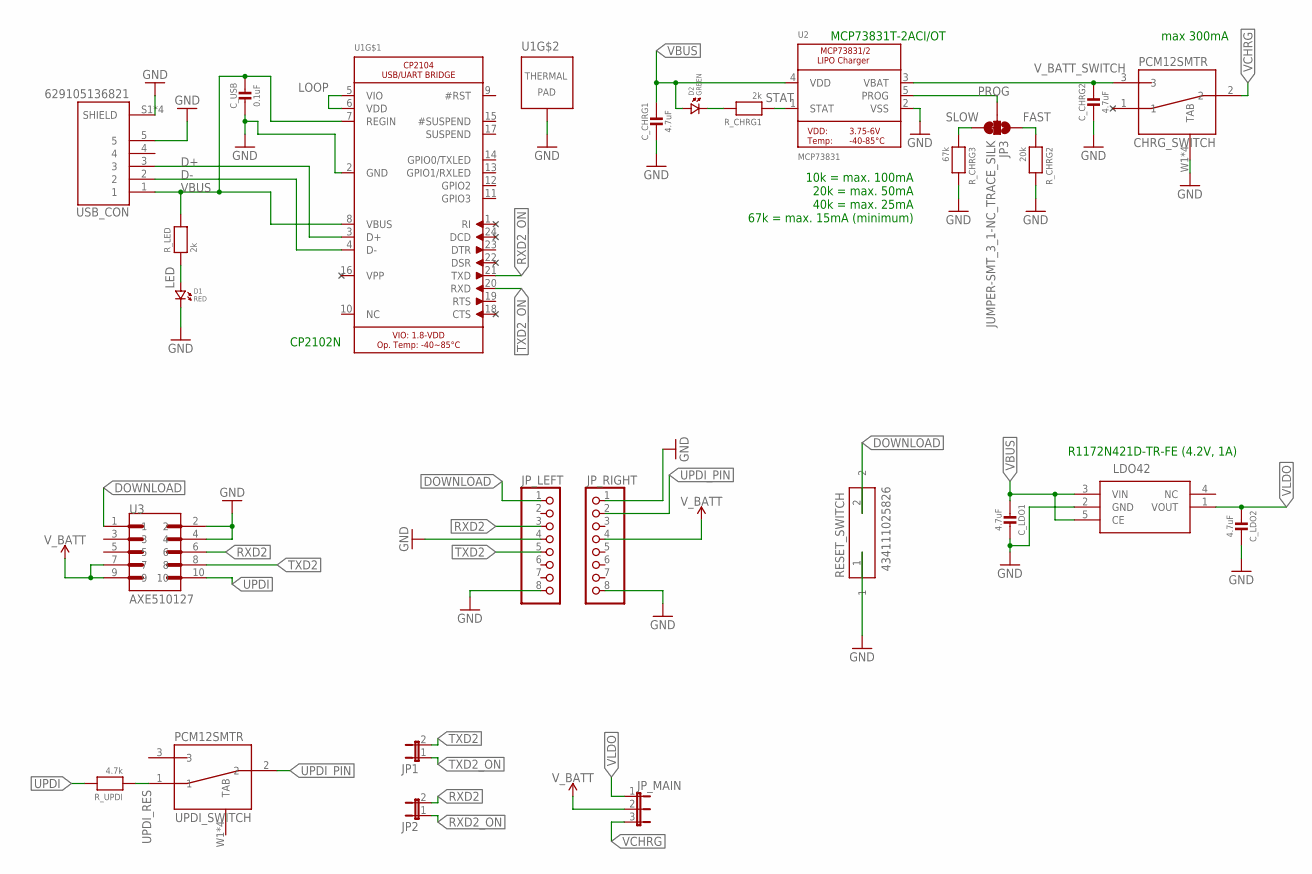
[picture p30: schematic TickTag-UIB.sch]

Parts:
CHRG_SWITCH: PCM12SMTR
C_CHRG1, C_CHRG2: 4.7uF; MICROBUILDER__0402MP
C_LDO1, C_LDO2: 4.7uF; MICROBUILDER__0402MP
C_USB: 0.1uF; MICROBUILDER__0402MP
D1: RED; CMONR_STANDARDPARTS_0402.LED
D2: GREEN; CMONR_STANDARDPARTS_0402.LED
JP1, JP2: JP1E; JP1
JP3: JUMPER-SMT_3_1-NC_TRACE_SILK; SMT-JUMPER_3_1-NC_TRACE_SILK
JP_LEFT: PINHD-1X8BIG; 1X08-BIG
JP_MAIN: JP2E; JP2
JP_RIGHT: PINHD-1X8BIG; 1X08-BIG
LDO42: R1172N421D-TR-FE
RESET_SWITCH: 434111025826
R_CHRG1: 2k; MICROBUILDER__0402MP
R_CHRG2: 20k; MICROBUILDER__0402MP
R_CHRG3: 67k; MICROBUILDER__0402MP
R_LED: 2k; MICROBUILDER__0402MP
R_UPDI: 4.7k; MICROBUILDER__0402MP
U1: CP2104_MICROBUILDER_CP2104; CP2104_MICROBUILDER_QFN24_4MM_SMSC
U2: MCP73831; MICROBUILDER_SOT23-5
U3: AXE510127
UPDI_SWITCH: PCM12SMTR
USB_CON: 629105136821; WE_629105136821

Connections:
D+: U1.3 (D+), USB_CON.3
D-: U1.4 (D-), USB_CON.2
DOWNLOAD: JP_LEFT.1, RESET_SWITCH.2, U3.1
FAST: JP3.1, R_CHRG2.1
GND: CHRG_SWITCH.W1 (TAB), CHRG_SWITCH.W2 (TAB), CHRG_SWITCH.W3 (TAB), CHRG_SWITCH.W4 (TAB), C_CHRG1.2, C_CHRG2.2, C_LDO1.1, C_LDO2.1, C_USB.2, D1.P$2 (2), JP_LEFT.4, JP_LEFT.8, JP_RIGHT.1, JP_RIGHT.8, LDO42.2 (GND), RESET_SWITCH.1, R_CHRG2.2, R_CHRG3.2, U1.2 (GND), U1.THERM (TP), U2.2 (VSS), U3.2, U3.4, USB_CON.5, USB_CON.S1 (SHIELD), USB_CON.S2 (SHIELD), USB_CON.S3 (SHIELD), USB_CON.S4 (SHIELD)
LED: D1.P$1 (1), R_LED.1
LOOP: U1.5 (VIO), U1.6 (VDD)
PROG: JP3.2, U2.5 (PROG)
RXD2: JP2.2, JP_LEFT.3, U3.6
RXD2_ON: JP2.1, U1.21 (TXD)
SLOW: JP3.3, R_CHRG3.1
STAT: R_CHRG1.1, U2.1 (STAT)
STAT_BTW: D2.P$2 (2), R_CHRG1.2
TXD2: JP1.2, JP_LEFT.5, U3.8
TXD2_ON: JP1.1, U1.20 (RXD)
UPDI: R_UPDI.2, U3.10
UPDI_PIN: JP_RIGHT.2, UPDI_SWITCH.2
UPDI_RES: R_UPDI.1, UPDI_SWITCH.1
VBUS: C_CHRG1.1, C_LDO1.2, C_USB.1, D2.P$1 (1), LDO42.3 (VIN), LDO42.5 (CE), R_LED.2, U1.7 (REGIN), U1.8 (VBUS), U2.4 (VDD), USB_CON.1
VCHRG: CHRG_SWITCH.2, JP_MAIN.3
VLDO: C_LDO2.2, JP_MAIN.1, LDO42.1 (VOUT)
V_BATT: JP_MAIN.2, JP_RIGHT.4, U3.7, U3.9
V_BATT_SWITCH: CHRG_SWITCH.3, C_CHRG2.1, U2.3 (VBAT)

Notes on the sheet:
10k = max. 100mA 20k = max. 50mA 40k = max. 25mA 67k = max. 15mA (minimum)
max 300mA
CP2102N
MCP73831T-2ACI/OT
R1172N421D-TR-FE (4.2V, 1A)

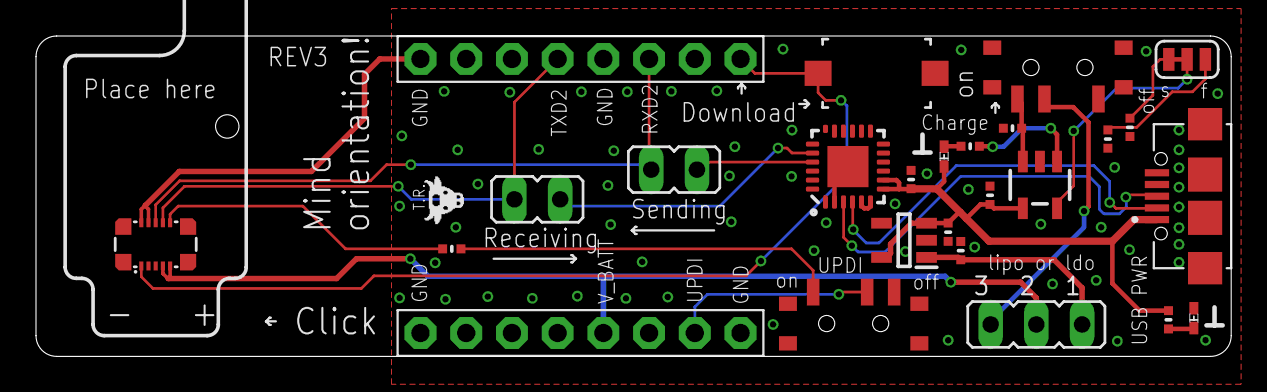
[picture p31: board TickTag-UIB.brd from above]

Board: 2 copper layers, 66.4 x 17.8 mm, 26 parts (0 on the bottom side), 23 nets.

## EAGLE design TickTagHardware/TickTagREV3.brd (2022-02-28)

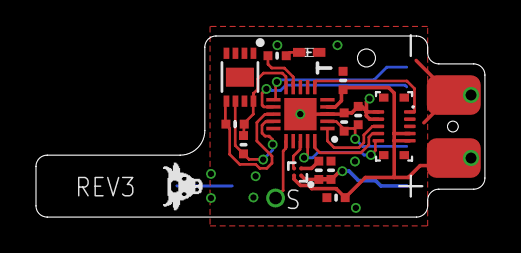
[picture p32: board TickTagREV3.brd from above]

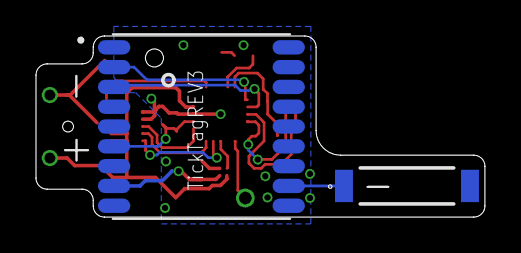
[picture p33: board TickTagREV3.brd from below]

Board: 2 copper layers, 24.9 x 10.1 mm, 18 parts (2 on the bottom side), 17 nets.

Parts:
ANT-CHIP: ANT1; SAMACSYS_PARTS_1575AT43A0040E
ATTINY: ATTINY1616-MFR; QFN40P300X300X90-21N
C1, C2: BATTERYSOLDERPAD
C_BCK1: 0.1uF; MICROBUILDER__0402MP
C_BCK2: 4.7uF; MICROBUILDER__0402MP
C_L701: 0.1uF; MICROBUILDER__0402MP
C_L702: 10uF; MICROBUILDER__0402MP
C_TINY: 1uF; MICROBUILDER__0402MP
C_TPS: 1uF; MICROBUILDER__0402MP
D_LED_GREEN: GREEN; CMONR_STANDARDPARTS_0402.LED
L70: L70; XCVR_L70
MEM: CAT24M01HU5I-GT3; SON50P300X200X55-9N
R_LED: 1k; MICROBUILDER__0402MP
R_SCL: 4.7k; MICROBUILDER__0402MP
R_SDA: 4.7k; MICROBUILDER__0402MP
U1: AXE610124
U6: TPS22916

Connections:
ANT_GNSS: ANT-CHIP.1, L70.11
DOWNLOAD: ATTINY.6, U1.1
GND: ATTINY.3, ATTINY.21, C2.1, C_BCK1.1, C_BCK2.1, C_L701.1, C_L702.1, C_TINY.1, C_TPS.2, D_LED_GREEN.P$2, L70.1, L70.10, L70.12, MEM.4, MEM.9, U1.2, U1.4, U6.B1
LED_GREEN: ATTINY.9, R_LED.2
unnamed: D_LED_GREEN.P$1, R_LED.1
POWER_L70: C_L701.2, C_L702.2, L70.8, U6.A1
POWER_L70_BCK: ATTINY.2, C_BCK1.2, C_BCK2.2, L70.6
POWER_L70_ON: ATTINY.18, U6.B2
POWER_MEMORY: ATTINY.10, MEM.8, R_SCL.2, R_SDA.2
RXD: ATTINY.11, L70.2
RXD2: ATTINY.1, U1.6
SCL: ATTINY.14, MEM.6, R_SCL.1
SDA: ATTINY.13, MEM.5, R_SDA.1
TXD: ATTINY.12, L70.3
TXD2: ATTINY.20, U1.8
UPDI: ATTINY.19, U1.10
V_BATT: ATTINY.4, C1.1, C_TINY.2, C_TPS.1, U1.7, U1.9, U6.A2

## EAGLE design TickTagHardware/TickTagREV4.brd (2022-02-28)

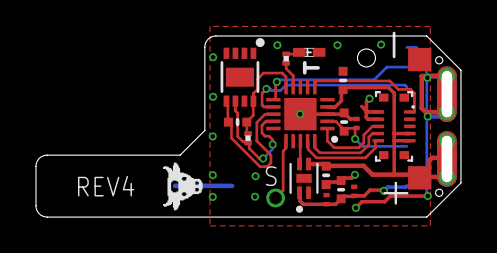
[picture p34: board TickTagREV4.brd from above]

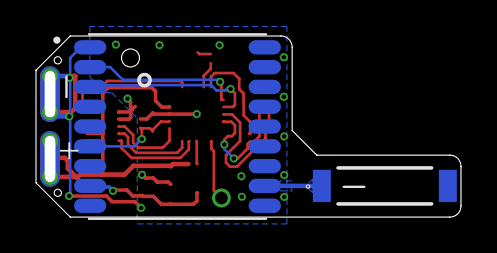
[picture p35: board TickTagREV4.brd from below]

Board: 2 copper layers, 23.6 x 10.1 mm, 19 parts (2 on the bottom side), 17 nets.

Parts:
ANT-CHIP: ANT1; SAMACSYS_PARTS_1575AT43A0040E
ATTINY: ATTINY1616-MFR; QFN40P300X300X90-21N
AXE: AXE610124
C_BCK1: 0.1 uF; C0201
C_BCK2: 4.7uF; MICROBUILDER__0402MP
C_L701: 0.1 uF; C0201
C_L702: 10uF; MICROBUILDER__0402MP
C_LS: 1uF; MICROBUILDER__0402MP
C_LS2: 0.1 uF; C0201
C_TINY: 1uF; MICROBUILDER__0402MP
D_LED_GREEN: GREEN; CMONR_STANDARDPARTS_0402.LED
L70: L70; XCVR_L70
LS: SIP32431DNP3-T1GE4; SON50P120X160X60-5N
MEM: CAT24M01HU5I-GT3; SON50P300X200X55-9N
R_LED: 1k; R0201
R_SCL: 4.7k; R0201
R_SDA: 4.7k; MICROBUILDER__0402MP
TP1, TP2: PTR1TP13SQ; TP13SQ

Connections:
ANT_GNSS: ANT-CHIP.1, L70.11
DOWNLOAD: ATTINY.6, AXE.1
GND: ATTINY.3, ATTINY.21, AXE.2, AXE.4, C_BCK1.2, C_BCK2.1, C_L701.2, C_L702.1, C_LS.1, C_LS2.2, C_TINY.1, D_LED_GREEN.P$2, L70.1, L70.10, L70.12, LS.2, LS.5, MEM.4, MEM.9, TP1.TP
LED_GREEN: ATTINY.9, R_LED.1
unnamed: D_LED_GREEN.P$1, R_LED.2
POWER_L70: C_L701.1, C_L702.2, C_LS2.1, L70.8, LS.1
POWER_L70_BCK: ATTINY.2, C_BCK1.1, C_BCK2.2, L70.6
POWER_L70_ON: ATTINY.18, LS.4
POWER_MEMORY: ATTINY.10, MEM.8, R_SCL.1, R_SDA.2
RXD: ATTINY.11, L70.2
RXD2: ATTINY.1, AXE.6
SCL: ATTINY.14, MEM.6, R_SCL.2
SDA: ATTINY.13, MEM.5, R_SDA.1
TXD: ATTINY.12, L70.3
TXD2: ATTINY.20, AXE.8
UPDI: ATTINY.19, AXE.10
V_BATT: ATTINY.4, AXE.7, AXE.9, C_LS.2, C_TINY.2, LS.3, TP2.TP

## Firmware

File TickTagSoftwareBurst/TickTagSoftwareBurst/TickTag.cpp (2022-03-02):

#include "TickTag.h"

//extern volatile static uint32_t millisElapsed;

void deviceInitPins() {
	// OUTPUT = lowest setting
	PORTA.DIR = (INPUT_DIR << PIN0_bp)	// PA0: UPDI
	| (OUTPUT_DIR << PIN1_bp)			// PA1: TXD2
	| (OUTPUT_DIR << PIN2_bp)			// PA2: RXD2
	| (OUTPUT_DIR << PIN3_bp)			// PA3: POWER_L70_BCK
	| (OUTPUT_DIR << PIN4_bp)			// PA4: **UNUSED**
	| (INPUT_DIR << PIN5_bp)			// PA5: DOWNLOAD (NEW: changed from OUTPUT to INPUT)
	| (OUTPUT_DIR << PIN6_bp)			// PA6: TIMER
	| (OUTPUT_DIR << PIN7_bp);			// PA7: **UNUSED**	
	PORTB.DIR = (OUTPUT_DIR << PIN0_bp)	// PB0: SCL
	| (OUTPUT_DIR << PIN1_bp)			// PB1: SDA
	| (OUTPUT_DIR << PIN2_bp)			// PB2: TXD
	| (INPUT_DIR << PIN3_bp)			// PB3: RXD
	| (OUTPUT_DIR << PIN4_bp)			// PB4: POWER_MEMORY
	| (OUTPUT_DIR << PIN5_bp);			// PB5: LED_GREEN
	PORTC.DIR = (OUTPUT_DIR << PIN0_bp)	// PC0: **UNUSED**
	| (OUTPUT_DIR << PIN1_bp)			// PC1: GPIO2 (A/ST)
	| (OUTPUT_DIR << PIN2_bp)			// PC2: GPIO1
	| (OUTPUT_DIR << PIN3_bp);			// PC3: POWER_L70_ON
	
	#if defined (__AVR_ATtiny1626__)
	// doesn't work
	//PORTA.PIN1CTRL = (0 << PORT_INVEN_bp) | (0 << PORT_PULLUPEN_bp) | (1 << PORT_ISC2_bp); // not inverted, no pull-up, disable input buffer (can't read input values), IMPORTANT, otherwise +30uA leakage
	//PORTA.PIN2CTRL = (0 << PORT_INVEN_bp) | (0 << PORT_PULLUPEN_bp) | (1 << PORT_ISC2_bp);
	#endif
	
	// unconnected pins: no pull-up, disable digital input buffer (can't measure input value) -> reduces current by around 1uA per pin in active (not sleeping)
	/*PORTA.PIN4CTRL = UNUSED_PIN_SETTING;
	PORTA.PIN7CTRL = UNUSED_PIN_SETTING;
	PORTC.PIN0CTRL = UNUSED_PIN_SETTING;
	PORTC.PIN1CTRL = UNUSED_PIN_SETTING;
	PORTC.PIN2CTRL = UNUSED_PIN_SETTING;*/
	
	// enable PULL-UPs
	//PORTA.PIN6CTRL |= PORT_PULLUPEN_bm;
	PORTA.PIN5CTRL = PORT_PULLUPEN_bm; // NEW: pullup enabled already in start
	
	// 67uA less @1MHz 3.6V, TCD shall use prescaled clock, not "raw OSC20M", divider is not relevant here, TCD disabled (bit 0)
	#if defined (__AVR_ATtiny1616__)
		TCD0.CTRLA = TCD_CLKSEL_SYSCLK_gc | TCD_CNTPRES_DIV1_gc; // only for ATTINY1616, not for ATTINY1606 or ATTINY1626
	#else
		// don't do it
	#endif
}

void deviceInitGPIO2PinInterruptInDeepSleep() {
	// REQUIRES IN MAIN
	/*
	ISR(PORTC_PORT_vect) { PORTC.INTFLAGS |= PORT_INT1_bm; }
	*/
	PORTC.DIR &= ~PIN1_bm; // set pin as input
	PORTC.PIN1CTRL = PORT_PULLUPEN_bm | PORT_ISC_BOTHEDGES_gc; // enable pull-up and interrupt
}

void deviceDeactivateGPIO2PinInterruptInDeepSleep() {
	PORTC.PIN1CTRL = 0; // disable pull-up and interrupt
	PORTC.DIR |= PIN1_bm; // set as output
}

void deviceInitDownloadPinInterruptInDeepSleep() {
	// REQUIRES IN MAIN
	/*
	ISR(PORTA_PORT_vect) { PORTA.INTFLAGS |= PORT_INT5_bm; }
	*/
	PORTA.PIN5CTRL |= PORT_ISC_BOTHEDGES_gc; // enable interrupt
}

volatile static uint32_t millisElapsed; // volatile because access in ISR

void deviceIncrementTimer() {
	millisElapsed++;
}

void deviceInitTimer() {
	// NEEDS IMPLEMENTATION OF THAT FUNCTION IN MAIN:
	/*
	ISR(TCA0_OVF_vect) {
		deviceIncrementTimer();
		TCA0.SINGLE.INTFLAGS = TCA_SINGLE_OVF_bm; // Clear the interrupt flag (to reset TCA0.CNT)
	}
	*/
	millisElapsed = 0;
	TCA0.SINGLE.INTCTRL = TCA_SINGLE_OVF_bm; // enable overflow interrupt
	TCA0.SINGLE.CTRLB = TCA_SINGLE_WGMODE_NORMAL_gc; // set Normal mode
	#if defined (__AVR_ATtiny1626__)
		// don't do it
	#else
		TCA0.SINGLE.EVCTRL &= ~(TCA_SINGLE_CNTEI_bm); // disable event counting
	#endif
	TCA0.SINGLE.PER = TIMER_TOP;
	TCA0.SINGLE.CTRLA = TCA_SINGLE_ENABLE_bm;
	sei();	
}

uint32_t deviceGetMillis() {
	uint32_t temp;
	ATOMIC_BLOCK(ATOMIC_RESTORESTATE) { temp = millisElapsed; }
	return temp;
}

void deviceStopTimer() {
	cli();
	TCA0.SINGLE.INTCTRL = 0;
	TCA0.SINGLE.CTRLA = 0; // disable timer in case it's running
	sei();	
}

void deviceL70powerOn() {
	//PORTC.DIR |= PIN3_bm; // output
	PORTC.OUTSET = PIN3_bm; // high
}

void deviceL70powerOff() {
	//PORTC.DIR |= PIN3_bm; // output
	PORTC.OUTCLR = PIN3_bm; // low
}

void deviceL70backupOn() {
	//PORTA.DIR |= PIN3_bm; // output
	PORTA.OUTSET = PIN3_bm; // high
}

void deviceL70backupOff() {
	//PORTA.DIR |= PIN3_bm; // output
	PORTA.OUTCLR = PIN3_bm; // low
}

void devicePowerMemoryAndI2COff() {
	////PORTB.DIR |= PIN4_bm; // output
	PORTB.OUTCLR = PIN4_bm; // low
}

void devicePowerMemoryAndI2COn() {
	////PORTB.DIR |= PIN4_bm; // output
	PORTB.OUTSET = PIN4_bm; // high
	_delay_ms(1); // according to datasheet: memory ready after 0.1ms
}

void deviceDisableBODInSleep() {
	// TODO: set registers in one step (setting CCP only once) -> use _PROTECTED_WRITE()?
	CCP = 0xD8; 								// configuration change protection -> 4 instructions time for change
	BOD.CTRLA &= ~(1 << BOD_SLEEP0_bp); 		// set 0 (disabled)
	CCP = 0xD8;									// configuration change protection -> 4 instructions time for change
	BOD.CTRLA &= ~(1 << BOD_SLEEP1_bp); 		// set 0 (disabled)
}

void deviceDeepSleep() {
	deviceStopTimer(); // in case it was running
	
	// disable I2C pull-ups (important, being set by I2C)
	PORTB.PIN0CTRL = 0;
	PORTB.PIN1CTRL = 0;
	
	set_sleep_mode(SLEEP_MODE_PWR_DOWN); 		// deep sleep
	power_all_disable();   						// power off ADC, Timer 0 and 1, serial interface
	cli(); 										// disable interrupts for CCP = noInterrupts() function in Arduino
	sleep_enable();								// enable

	//disableBODInSleep();						// disable BOD totally (if not already set by fuses)

	sei();           							// enable interrupts again = interrupts() function in Arduino
	sleep_cpu();            					// stop
	sleep_disable();        					// wake again
	power_all_enable();     					// power everything back on
}

void deviceStandbySleep() {
	deviceStopTimer(); // in case it was running
	
	// disable I2C pull-ups (important, being set by I2C)
	PORTB.PIN0CTRL = 0;
	PORTB.PIN1CTRL = 0;
	
	set_sleep_mode(SLEEP_MODE_STANDBY); 		// standby sleep
	sleep_enable();								// enable
	sleep_cpu();            					// stop
}

void deviceInitInternalRTCInterrupt(uint16_t seconds) {
	// needs implementation of interrupt routine and can only wakeup from standby sleep (RTC running):
	//ISR(RTC_CNT_vect) { RTC.INTFLAGS = RTC_OVF_bm; }
	// accuracy depends on PRESCALER -> smaller = better, but then max seconds smaller
	// currently (256 prescaler = 4Hz CNT updates): min. 0.25s - max. 2^16 / 4 = 16384 seconds = 4.55hrs
	cli();												// disable global interrupts
	while(RTC.STATUS > 0) {} 							// wait for all register to be synchronized
	RTC.CNT = 0;										// reset counter value
	while(RTC.STATUS > 0) {}							// wait until CNT is reset
	RTC.PER = seconds * 4; 								// 16 bit wide maximum value, sets seconds between wakes (maximum value of cnt)
	RTC.CLKSEL = RTC_CLKSEL_INT1K_gc; 					// running at 1.024Hz
	RTC.CTRLA = RTC_PRESCALER_DIV256_gc 				// prescaler, e.g. set to 256 -> 1024 / 256 = incrementing CNT with 4Hz
		| 1 << RTC_RTCEN_bp         					// enable RTC
		| 1 << RTC_RUNSTDBY_bp;     					// run in standby, increases standby power consumption
	RTC.INTCTRL = 1 << RTC_OVF_bp; 						// overflow interrupt
	sei();												// enable global interrupts			
}

#if defined (__AVR_ATtiny1626__)
int16_t getInternalTemperature() {
	uint16_t adc_reading;
	uint16_t temperature_in_K;
	int16_t temperature_in_degC;
	
	ADC0.CTRLA = ADC_ENABLE_bm;
	ADC0.CTRLB = ADC_PRESC_DIV2_gc; // fCLK_ADC = 3.333333/2 MHz
	ADC0.CTRLC = ADC_REFSEL_1024MV_gc | (TIMEBASE_VALUE << ADC_TIMEBASE_gp);
	ADC0.CTRLE = TEMPSENSE_SAMPDUR;

	ADC0.MUXPOS = ADC_MUXPOS_TEMPSENSE_gc; // ADC Internal Temperature Sensor
	ADC0.COMMAND = ADC_MODE_SINGLE_12BIT_gc; // Single 12-bit mode

	int8_t sigrow_offset = SIGROW.TEMPSENSE1; // Read signed offset from signature row
	uint8_t sigrow_gain = SIGROW.TEMPSENSE0; // Read unsigned gain/slope from signature row

	ADC0.COMMAND |= ADC_START_IMMEDIATE_gc; // Start ADC conversion
	while(!(ADC0.INTFLAGS & ADC_RESRDY_bm)); // Wait until conversion is done

	// Calibration compensation as explained in the data sheet
	adc_reading = ADC0.RESULT >> 2; // 10-bit MSb of ADC result with 1.024V internal reference
	uint32_t temp = adc_reading - sigrow_offset;
	
	temp *= sigrow_gain; // Result might overflow 16-bit variable (10-bit + 8-bit)
	temp += 0x80; // Add 256/2 to get correct integer rounding on division below
	temp >>= 8; // Divide result by 256 to get processed temperature in Kelvin
	temperature_in_K = temp;
	temperature_in_degC = temperature_in_K - 273;
	
	ADC0.CTRLA = 0; // disable ADC
	return temperature_in_degC;
}
#endif

uint16_t deviceReadSupplyVoltage() {
	#if defined (__AVR_ATtiny1626__)
		uint32_t res;
	
		ADC0.CTRLA = ADC_ENABLE_bm; // enable ADC
		//ADC0.CTRLB = ADC_PRESC_DIV2_gc; // DEFAULT setting
		ADC0.CTRLC = VREF_AC0REFSEL_1V024_gc | (TIMEBASE_VALUE << ADC_TIMEBASE0_bp); // Vref = 1.024V
		ADC0.CTRLE = 100; // sample duration ((100 * 2) / F_CPU seconds), 1 MHz = 0.2ms
		ADC0.MUXPOS = ADC_MUXPOS_DAC_gc; // using DAC as MUX voltage, ADC_MUXPOS_VDDDIV10_gc doesn't work
		ADC0.COMMAND = ADC_MODE_SINGLE_12BIT_gc; // single mode with 12 bit
		ADC0.COMMAND |= ADC_START_IMMEDIATE_gc; // start conversion

		while(true) {
			if(ADC0.INTFLAGS & ADC_RESRDY_bm) { // wait until measurement done
				res = (uint32_t) ADC0.RESULT; // get raw adc result
				if(res == 0) { res = 1; }
				res = (4096UL * 1024UL) / res; // convert result to mV
				break;
			}
		}
		ADC0.CTRLA = 0; // disable ADC
		return ((uint16_t) res);
	#else
		// the App Note AN2447 uses Atmel Start to configure Vref but we'll do it explicitly in our code
		VREF.CTRLA = VREF_ADC0REFSEL_1V1_gc;  			// set the Vref to 1.1V

		// the following section is directly taken from Microchip App Note AN2447 page 13     
		ADC0.MUXPOS = ADC_MUXPOS_INTREF_gc; 	   		// ADC internal reference, the Vbg
    
		// take care! ADC needs certain peripheral clock speed (50kHz - 1.5MHz after ADC_PRESC_..) for maximum resolution, here CLOCK = 1MHz divided by 4 = 0.25MHz = within range of 50kHz - 1.5MHz
		ADC0.CTRLC = ADC_PRESC_DIV4_gc					// CLK_PER divided by certain value
			| ADC_REFSEL_VDDREF_gc						// Vdd (Vcc) be ADC reference
			| 0 << ADC_SAMPCAP_bp;						// Sample Capacitance Selection: disabled
		ADC0.CTRLA = 1 << ADC_ENABLE_bp					// ADC Enable: enabled
			| 1 << ADC_FREERUN_bp						// ADC Free run mode: enabled
			| ADC_RESSEL_10BIT_gc;						// 10-bit mode
		//ADC0.CTRLD = ADC_INITDLY_DLY256_gc;			// init delay 256 CLK_ADC cycles (important!)
		ADC0.COMMAND |= 1;								// start running ADC
		_delay_ms(5);									// REALLY?! <- YES, important to wait for first measurement!
	
		#if (VCC_DO_NOT_USE_AVERAGE == true)
			uint32_t vcc, temp;
			while(true) {
				if(ADC0.INTFLAGS) {
					temp = (uint32_t) ADC0.RES;
					if(temp == 0) { temp = 1; }
					vcc = (1024UL * 1100UL) / temp;
					break;
				}
			}
		#else
			// read some samples and calculate average
			uint32_t vcc = 0, temp = 0;
			for(uint8_t i=0; i<VCC_SAMPLES; i++) {
				if(ADC0.INTFLAGS) {							// if an ADC result is ready
					temp = (uint32_t) ADC0.RES;				// e.g. 450 for 2.5V
					if(temp == 0) { temp = 1; }
					vcc += (1024UL * 1100UL) / temp; 		// 1100 = 1.1V
					_delay_ms(VCC_SAMPLE_DELAY_MS);
				}		
			}
			vcc /= VCC_SAMPLES;								// build integer average
		#endif
		// disable ADC again
		ADC0.CTRLA = 0 << ADC_ENABLE_bp					// ADC Enable: enabled (seems okay) -> no, changed that to 0! should be disabled!
			| 0 << ADC_FREERUN_bp						// ADC Free run mode: disabled (important for sleep)
			| ADC_RESSEL_10BIT_gc;						// 10-bit mode
			 
		#if defined (__AVR_ATtiny1606__)
			if(vcc >= 60) { vcc = vcc - 60; } // 1606 ADC seems to measure voltage higher than expected (only tested with one board)
		#endif
		          
		return (uint16_t) vcc;
	#endif
}
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

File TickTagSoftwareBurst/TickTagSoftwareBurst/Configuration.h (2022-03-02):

#ifndef CONFIGURATION_H_
#define CONFIGURATION_H_

#define TRACKING_MODE_NORMAL								0xDD
#define TRACKING_MODE_TEST									0xFF

/** ------ Important configuration ------ */
/** Important configuration - general */
#define SOFTWARE_VERSION									201
#define DEBUGGING											true		// false, if true forwards RX from GPS to USB breakout board
#define TRACKING_MODE										TRACKING_MODE_NORMAL // TRACKING_MODE_NORMAL or TRACKING_MODE_TEST
#define DOUBLE_CHECK_EEPROM_AFTER_SETTING					true		// false, double check if written value is correct (saves flash memory)
#define LED_ON_AFTER_GETTING_FIRST_TIME_AND_NIGHT			true		// if getting the very first fix (blinking) and is night time, turn LED on for 4 seconds

/** Important configuration - battery management */		
#define MIN_VOLTAGE_UNDER_LOAD								3050U		// unit: mV, threshold for exiting under load! GPS only works down to 3V
#define FIRST_SLEEP_TIME_SECONDS_WHEN_VOLTAGE_INCORRECT		60U			// 60U (1min), max. 16383 = 4.55hrs, very first under voltage in tracking just sleep a bit, keeping backup power on											
#define SLEEP_TIME_SECONDS_WHEN_VOLTAGE_INCORRECT			1800U		// 1800U (30min), max. 16383 = 4.55hrs
#define FIRST_START_DELAY_SECONDS							3			// 3, debounce a bit when soldering lipo

/** Important configuration - timeout for both modes */	
#define GET_FIX_TIMEOUT_NOT_EVEN_TIME_SECONDS				120			// 120, timeout triggered when did not even get a valid time (year still 80, hour = 0, minute < 3)
#define GET_FIX_SLEEP_LONGER_AFTER_TIMEOUT					true		// true, when timeout was triggered: sleep for GET_FIX_SLEEP_LONGER_AFTER_TIMEOUT_SECONDS instead of normal GPS frequency
#define GET_FIX_SLEEP_LONGER_AFTER_TIMEOUT_SECONDS			900U		// 900U = 15min, sleep for that time when timeout happened, keep backup power on

/** Important configuration - "sometimes mode" (frequency > 5) */	
#define GET_FIX_TIMEOUT_SECONDS								300			// 300, only when tracking frequency > 5 ("sometimes"), timeout until GPS attempt is canceled
#define WAIT_TIME_FIRST_FIX_SECONDS							30			// 30, only when tracking frequency > 5 ("sometimes"), always wait that time when getting first fix in session to collect orbit data
#define MAX_WAIT_ON_GOOD_HDOP_SECONDS						9			// 9, only when tracking frequency > 5 ("sometimes"), maximum wait time after fix in case HDOP is not good enough

/** Important configuration - "always-on mode" (frequency = 1 .. 5) */	
#define USE_FLP_MODE										true		// true, fitness low power mode (only 1hz), technically works in sometimes mode as well, but observed long fix times -> suitable for 1hz mode only

/** Important configuration - night time */
#define SLEEP_TIME_DURING_NIGHT								120U		// 120U (2min), max. 16383 = 4.55hrs: 1min = 1.09uA, 2min = 1.02uA, 3min = 0.99uA, 4min = 0.98uA, 5min = 0.97uA
#define BACKUP_POWER_ON_DURING_NIGHT_TIME					false		// false, keeping backup power on also at night time

/** Important configuration - geo-fencing */
#define GEOFENCING_LIMIT									300			// 300, 300 = roughly 300 meters, difference between 5 digit lat/lon (1 = 1.11m difference, 10 = 11.1m difference, 100 = 111m difference)
#define GEOFENCING_OR_ERROR_WAIT_TIME_SECONDS				600			// 600, when error detected or when geo-fencing active: wait for that amount of time (backup power on) before tracking again
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

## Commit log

2022-02-28 added hardware files
    [BOM-TickTagREV3.xlsx, BOM-TickTagREV3_Corrected.xls, BOM-TickTagREV4.xlsx, BOMTickTag-UIB.xlsx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]
2022-03-02 firmware upload
    [TTHousing165mAh_Bottom.stl, TTHousing165mAh_Lid.stl, TTHousing30mAhV2_Bottom.stl, TTHousing30mAhV2_Lid.stl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]
2022-06-08 added data from experiments
    [20210706_MyotisMyotis_Tag03_29_fixes.csv, 20210706_MyotisMyotis_Tag04_241_fixes.csv, 20210706_MyotisMyotis_Tag09_75_fixes.csv, 20210706_MyotisMyotis_Tag12_410_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]
2022-09-20 added fuse writing for ATTINY1616 (alternative to 1626), removed confusing comments in schematics
    [TickTagREV3.sch, TickTagREV4.sch]
2022-09-20 corrected BOMs
    [BOM-TickTagREV3.xls, BOM-TickTagREV3.xlsx, BOM-TickTagREV3_Corrected.xls, BOM-TickTagREV4.xlsx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]
2024-06-21 added awesome housings for UIB and tags (made by mark holton)

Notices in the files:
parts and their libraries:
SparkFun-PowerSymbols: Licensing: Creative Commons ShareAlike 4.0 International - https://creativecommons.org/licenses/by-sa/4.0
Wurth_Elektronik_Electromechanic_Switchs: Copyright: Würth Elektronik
